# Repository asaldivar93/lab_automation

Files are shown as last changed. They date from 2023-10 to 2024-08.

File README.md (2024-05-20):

## PWM Channels

To control PWM channels you have to create an Output class instance for each channel. The board has up to 6 channels.

```C++
#define N_OUTPUTS 6

Output CH_0(0, PIN_CH0, "pwm", MANUAL, 0);
Output CH_1(1, PIN_CH1, "pwm", MANUAL, 0);
Output CH_2(2, PIN_CH2, "pwm", MANUAL, 0);
Output CH_3(3, PIN_CH3, "pwm", MANUAL, 0);
Output CH_4(4, PIN_CH4, "pwm", MANUAL, 0);
Output CH_5(5, PIN_CH5, "pwm", MANUAL, 0);
Output outputs[N_OUTPUTS] = {CH_0, CH_1, CH_2, CH_3, CH_4, CH_5};
```

Channels can be controled in 4 different modes: {MANUAL, TIMER, PID, ONOFF}. You can initialize this control mode through setter functions.

```C++
Output::set_manual_output(int value);
Output::set_timer(int time_on, int time_off, int value);
Output::set_pid(float *input_value, float setpoint);
Output::set_onoff(float *input_value, int lb, int ub, int value);
```

Example:

```C++
void setup(){
  ...
  outputs[2].set_timer(10, 60, 255);
  ...
}
```

Which is equivalent to doing this:

```C++
void setup(){
  ...
  CH_2.set_timer(10, 60, 255);
  ...
}
```

The PID and ONOFF setters expect a pointer to the measured variable:
```C++
void setup(){
  ...
  outputs[2].set_pid(&inputs[1].value, 50.5);
  outputs[3].set_pid(&inputs[3].value, 1, 1.5, 255);
  ...
}
```
### PID control

The PID controler has important parameters that need to be defined during MCU initialization. This parameters have default values:

- PWM_min_vaule = 0
- PWM_max_value = 255
- Sampling time in microseconds = 250000 (0.250s)
- PID constants:
  - Kp = 100, Ki = 0.2, Kd = 0.

The PID controler uses a simple g-h filter to smooth very noisy signals. The filter uses this formula:

```C++
filtered_input[k] = alpha * current_input + (1 - alpha) * filtered_input[k - 1]
```
where *alpha* [0, 1] controls the strength of the smoothing. *alpha* = 1 **no smoothing at all**, *alpha* close to 0 **very strongth smoothing**. By **default** *alpha* = 0.01.

The default values were tuned to control the temperature of a water reservoir using an external electrical resistance and have been tested to heat water volumes between 50mL and 2L.

These parameters are initialized through setter functions:

```C++
Output::set_sample_time_us(uint32_t sample_time_us);
Output::set_pid_tunings(float Kp, float Ki, float Kd);
Output::set_output_limits(float min, float max);
Output::set_gh_filter(float alpha);
```
example:

```C++
void setup(){
  ...
  outputs[2].set_sample_time_us(250000);
  outputs[2].set_pid_tunings(100, 0.2, 0.);
  outputs[2].set_output_limits(0, 240);
  outputs[2].set_gh_filter(0.01);
  outputs[2].set_pid(&inputs[1].value, 50.5);
  ...
}
```

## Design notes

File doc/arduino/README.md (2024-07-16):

## PWM Channels

To control PWM channels you have to create an Output class instance for each channel. The board has up to 6 channels.

```C++
#define N_PWM 6

Output CH_0(0, PIN_CH0, "pwm", MANUAL, 0);
Output CH_1(1, PIN_CH1, "pwm", MANUAL, 0);
Output CH_2(2, PIN_CH2, "pwm", MANUAL, 0);
Output CH_3(3, PIN_CH3, "pwm", MANUAL, 0);
Output CH_4(4, PIN_CH4, "pwm", MANUAL, 0);
Output CH_5(5, PIN_CH5, "pwm", MANUAL, 0);
Output outputs[N_OUTPUTS] = {CH_0, CH_1, CH_2, CH_3, CH_4, CH_5};
```

Channels can be controled in 4 different modes: {MANUAL, TIMER, PID, ONOFF}. You can initialize this control mode through setter functions.

```C++
Output::set_manual_output(int value);
Output::set_timer(int time_on, int time_off, int value);
Output::set_pid(float *input_value, float setpoint);
Output::set_onoff(float *input_value, int lb, int ub, int value);
```

Example:

```C++
void setup(){
  ...
  outputs[2].set_timer(10, 60, 255);
  ...
}
```

Which is equivalent to doing this:

```C++
void setup(){
  ...
  CH_2.set_timer(10, 60, 255);
  ...
}
```

The PID and ONOFF setters expect a pointer to the measured variable:
```C++
void setup(){
  ...
  outputs[2].set_pid(&inputs[1].value, 50.5);
  outputs[3].set_pid(&inputs[3].value, 1, 1.5, 255);
  ...
}
```
### PID control

The PID controler has important parameters that need to be defined during MCU initialization. This parameters have default values:

- PWM_min_vaule = 0
- PWM_max_value = 255
- Sampling time in microseconds = 250000 (0.250s)
- PID constants:
  - Kp = 100, Ki = 0.2, Kd = 0.

The PID controler uses a simple g-h filter to smooth very noisy signals. The filter uses this formula:

```C++
filtered_input[k] = alpha * current_input + (1 - alpha) * filtered_input[k - 1]
```
where *alpha* [0, 1] controls the strength of the smoothing. *alpha* = 1 **no smoothing at all**, *alpha* close to 0 **very strongth smoothing**. By **default** *alpha* = 0.01.

The default values were tuned to control the temperature of a water reservoir using an external electrical resistance and have been tested to heat water volumes between 50mL and 2L.

These parameters are initialized through setter functions:

```C++
Output::set_sample_time_us(uint32_t sample_time_us);
Output::set_pid_tunings(float Kp, float Ki, float Kd);
Output::set_output_limits(float min, float max);
Output::set_gh_filter(float alpha);
```
example:

```C++
void setup(){
  ...
  outputs[2].set_sample_time_us(250000);
  outputs[2].set_pid_tunings(100, 0.2, 0.);
  outputs[2].set_output_limits(0, 240);
  outputs[2].set_gh_filter(0.01);
  outputs[2].set_pid(&inputs[1].value, 50.5);
  ...
}
```
## I2C Sensors

The board has a TCA9544 I2C multiplexer of 4 channels. This multiplexer allows reading sensors with the same address. You can control the multiplexer with the **Sensors** class

```C++
uint8_t multiplexer_address = 0x70;
float temperature;
Sensors sensors(multiplexer_address);

void setup(){
  Wire.begin();
  Serial.begin(9600);
}

void loop(){
  sensors.set_multiplexer_channel(0);
  temperature = sensors.read_sen0546_temperature();
  Serial.println(temperature);
}
```

Sensors API reference:

```C++
// SEN0546 Temperature and humidity sensor
Sensors::read_sen0546_temperature();
Sensors::read_sen0546_humidity();

// SEN0322 Oxygen Sensor
Sensors::read_sen0322_address_0();
Sensors::read_sen0322_address_1();
Sensors::read_sen0322_address_2();
Sensors::read_sen0322_default();

// MPRLS Pressure sensor
Sensors::read_mprls();
Sensors::set_mprls_range(float p_min, float p_max);

// SEN0343 differential pressure
Sensors::read_sen0343_diffpressure();
```

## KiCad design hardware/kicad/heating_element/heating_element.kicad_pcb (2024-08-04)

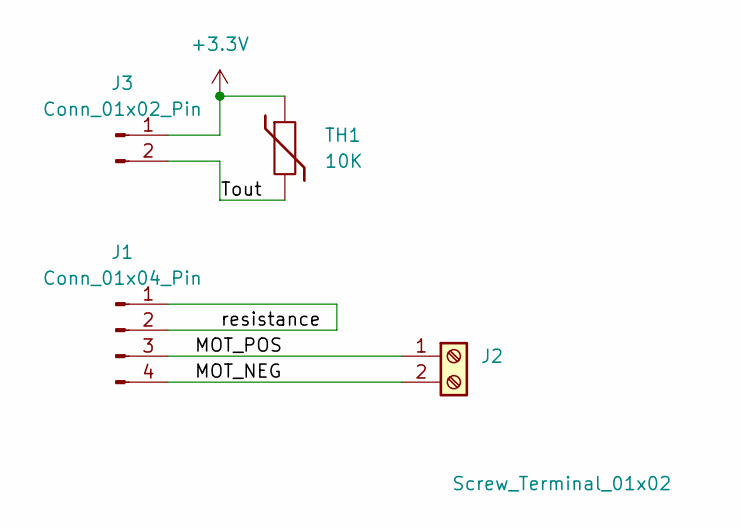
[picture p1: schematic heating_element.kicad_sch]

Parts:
J1: Conn_01x04_Pin; PinHeader_1x04_P2.54mm_Vertical
J2: Screw_Terminal_01x02; TerminalBlock_Phoenix_PT-1,5-2-5.0-H_1x02_P5.00mm_Horizontal
J3: Conn_01x02_Pin; PinHeader_1x02_P2.54mm_Vertical
TH1: 10K; R_Axial_DIN0204_L3.6mm_D1.6mm_P1.90mm_Vertical

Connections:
+3.3V: J3.1, TH1.1
/MOT_NEG: J1.4, J2.2
/MOT_POS: J1.3, J2.1
/Tout: J3.2, TH1.2
/resistance: J1.1, J1.2

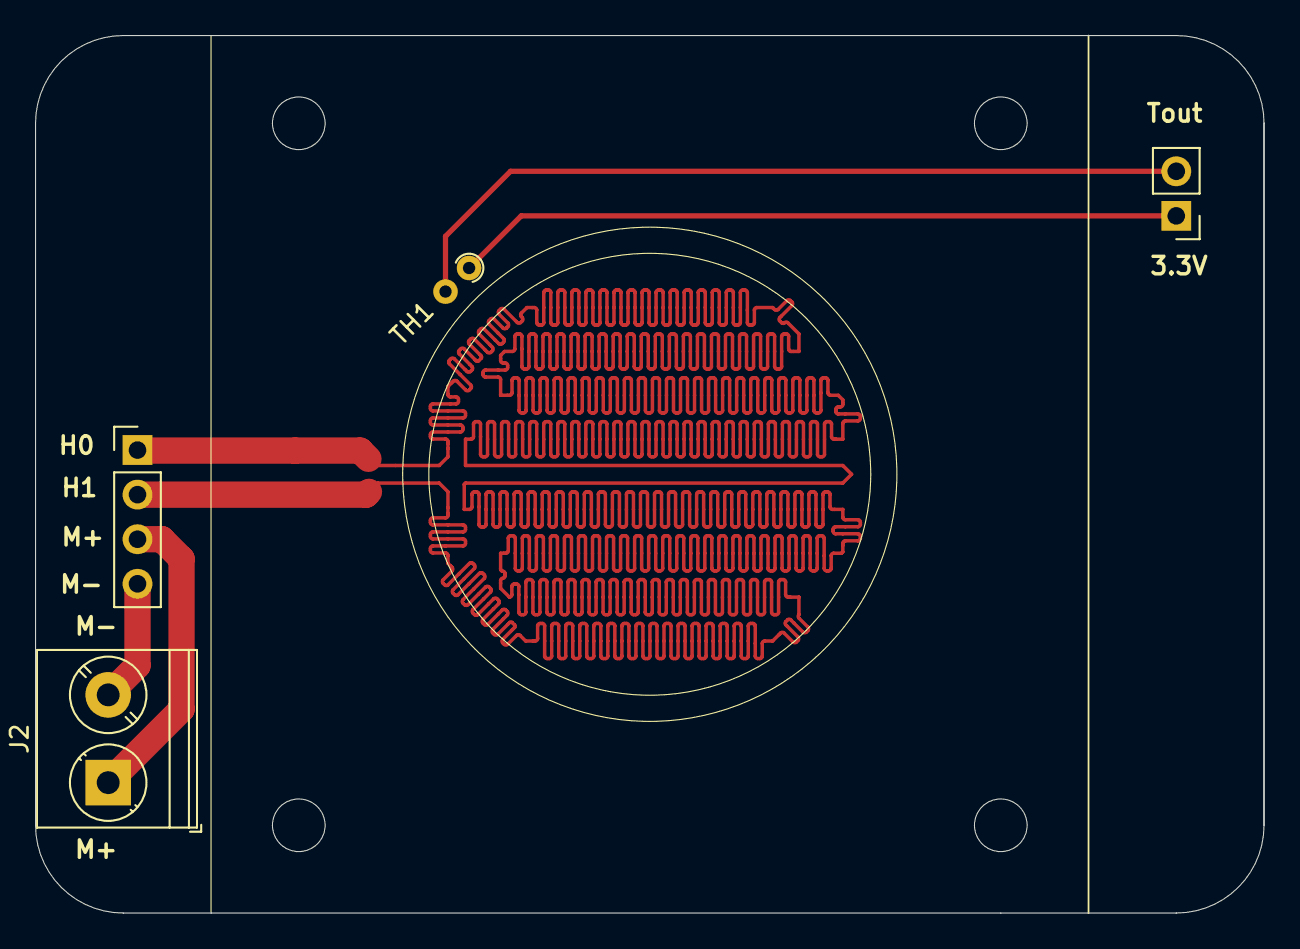
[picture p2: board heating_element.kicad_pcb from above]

Board: 2 copper layers, 70.0 x 50.0 mm, 4 parts (0 on the bottom side), 5 nets.

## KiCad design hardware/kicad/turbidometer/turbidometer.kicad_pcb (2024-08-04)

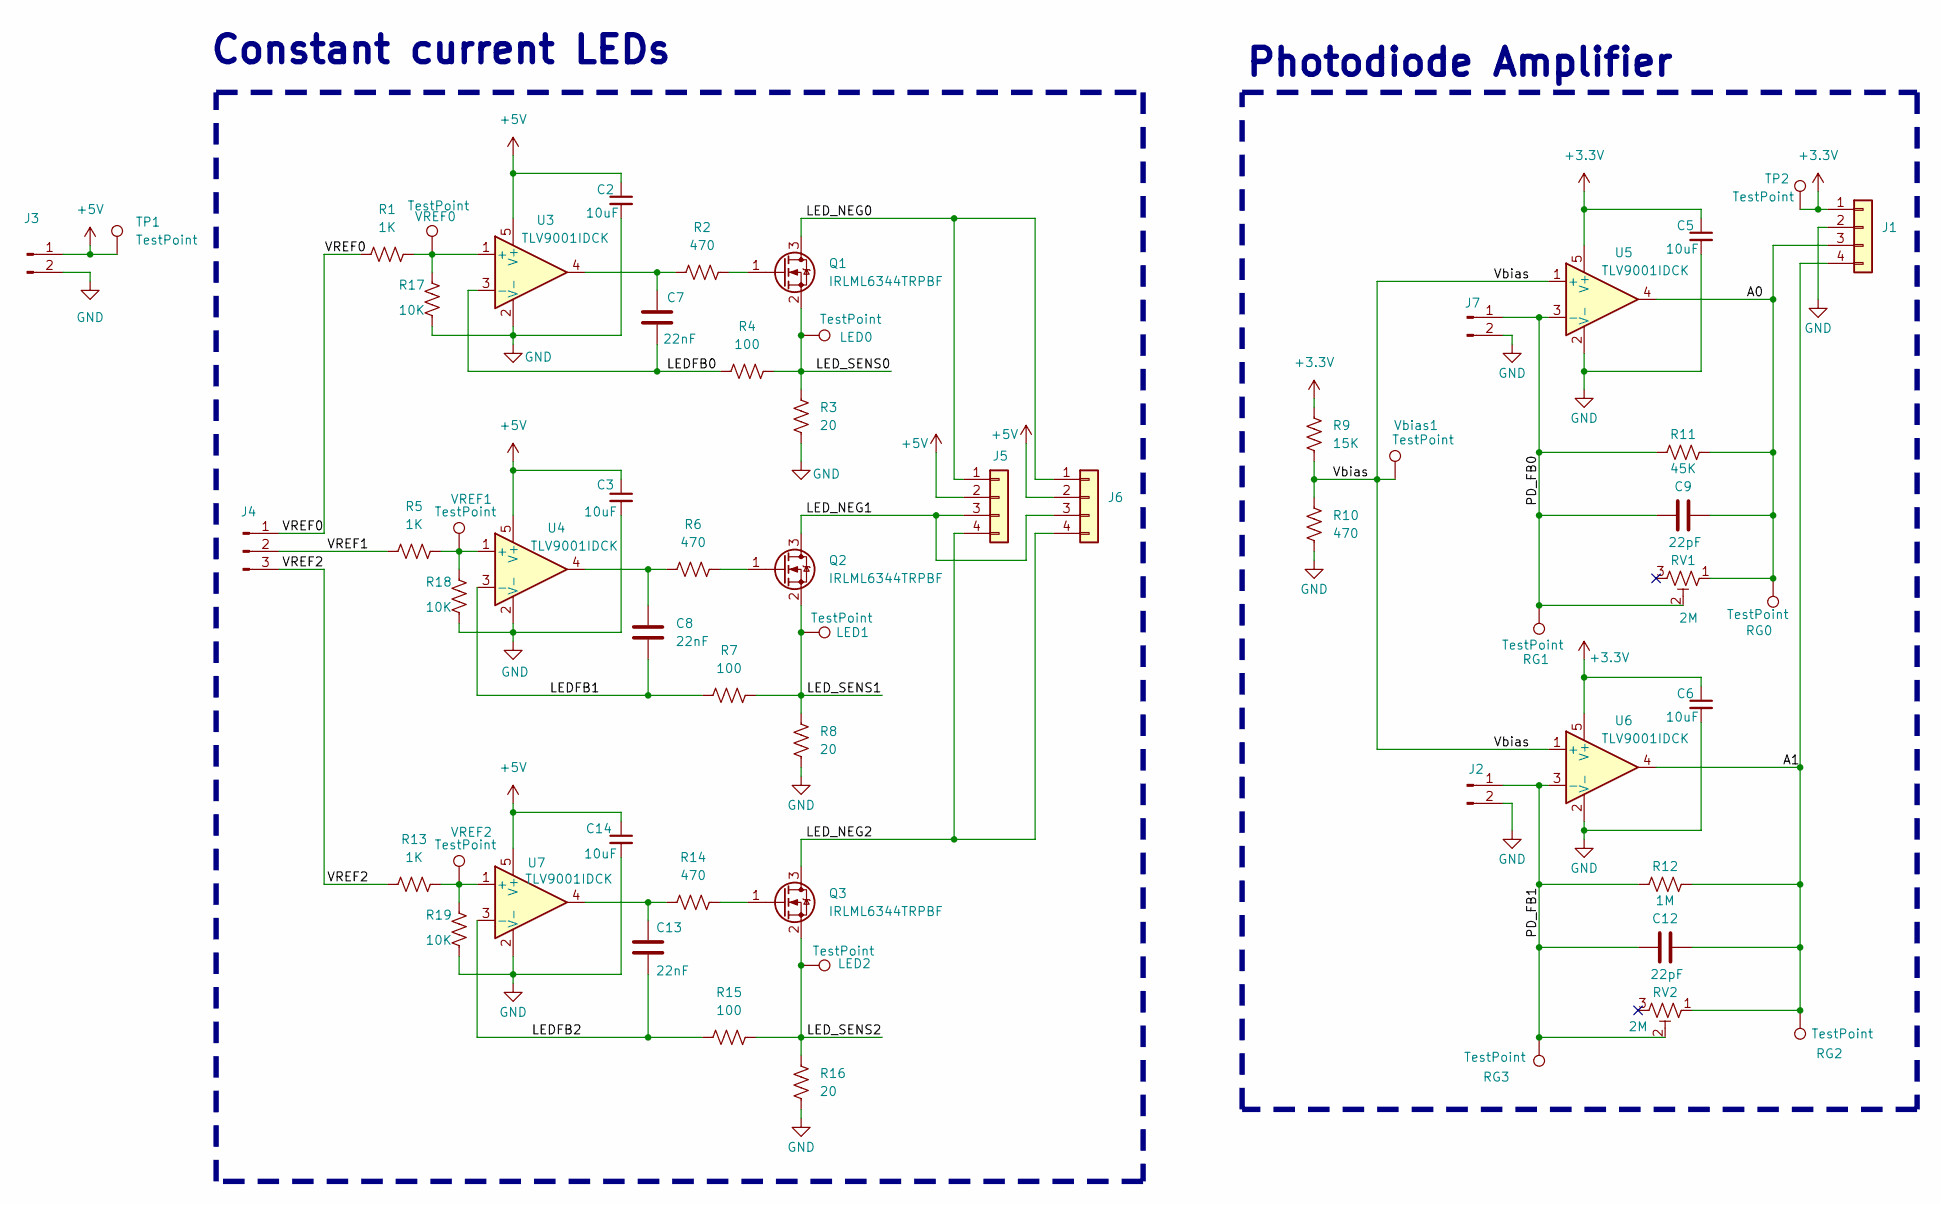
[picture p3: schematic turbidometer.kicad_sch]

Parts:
C2, C3, C5, C6, C14: 10uF; C_0805_2012Metric_Pad1.18x1.45mm_HandSolder
C7, C8, C13: 22nF; C_0805_2012Metric_Pad1.18x1.45mm_HandSolder
C9, C12: 22pF; C_0805_2012Metric_Pad1.18x1.45mm_HandSolder
J1: Conn_01x04; PinHeader_1x04_P2.54mm_Vertical
J2, J7: Conn_01x02_Pin; PinSocket_1x02_P2.54mm_Vertical
J3: Conn_01x02_Pin; PinHeader_1x02_P2.54mm_Vertical
J4: Conn_01x03_Pin; PinHeader_1x03_P2.54mm_Vertical
J5, J6: Conn_01x04; PinSocket_1x04_P2.54mm_Vertical
LED0, LED1, LED2: TestPoint; TestPoint_THTPad_1.5x1.5mm_Drill0.7mm
Q1, Q2, Q3: IRLML6344TRPBF; SOT-23_Handsoldering
R1, R5, R13: 1K; R_0805_2012Metric_Pad1.20x1.40mm_HandSolder
R2, R6, R10, R14: 470; R_0805_2012Metric_Pad1.20x1.40mm_HandSolder
R3, R8, R16: 20; R_0805_2012Metric_Pad1.20x1.40mm_HandSolder
R4, R7, R15: 100; R_0805_2012Metric_Pad1.20x1.40mm_HandSolder
R9: 15K; R_0805_2012Metric_Pad1.20x1.40mm_HandSolder
R11: 45K; R_0805_2012Metric_Pad1.20x1.40mm_HandSolder
R12: 1M; R_0805_2012Metric_Pad1.20x1.40mm_HandSolder
R17, R18, R19: 10K; R_0805_2012Metric_Pad1.20x1.40mm_HandSolder
RG0, RG1, RG2, RG3: TestPoint; TestPoint_THTPad_1.5x1.5mm_Drill0.7mm
RV1, RV2: 2M; Potentiometer_Bourns_3214W_Vertical
TP1, TP2: TestPoint; TestPoint_Pad_1.0x1.0mm
U3, U4, U5, U6, U7: TLV9001IDCK; SOT-353_SC-70-5
VREF0, VREF1, VREF2: TestPoint; TestPoint_THTPad_1.5x1.5mm_Drill0.7mm
Vbias1: TestPoint; TestPoint_Pad_1.0x1.0mm

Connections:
+3.3V: C5.1, C6.1, J1.1, R9.1, TP2.1, U5.5 (V+), U6.5 (V+)
+5V: C2.1, C3.1, C14.1, J3.1, J5.2, J6.2, TP1.1, U3.5 (V+), U4.5 (V+), U7.5 (V+)
/A0: C9.2, J1.3, R11.1, RG0.1, RV1.1, U5.4
/A1: C12.2, J1.4, R12.1, RG2.1, RV2.1, U6.4
/LEDFB0: C7.2, R4.2, U3.3 (-)
/LEDFB1: C8.2, R7.2, U4.3 (-)
/LEDFB2: C13.2, R15.2, U7.3 (-)
/LED_NEG0: J5.1, J6.1, Q1.3 (D)
/LED_NEG1: J5.3, J6.3, Q2.3 (D)
/LED_NEG2: J5.4, J6.4, Q3.3 (D)
/LED_SENS0: LED0.1, Q1.2 (S), R3.1, R4.1
/LED_SENS1: LED1.1, Q2.2 (S), R7.1, R8.1
/LED_SENS2: LED2.1, Q3.2 (S), R15.1, R16.1
/PD_FB0: C9.1, J7.1, R11.2, RG1.1, RV1.2, U5.3 (-)
/PD_FB1: C12.1, J2.1, R12.2, RG3.1, RV2.2, U6.3 (-)
/VREF0: J4.1, R1.2
/VREF1: J4.2, R5.2
/VREF2: J4.3, R13.2
/Vbias: R9.2, R10.1, U5.1 (+), U6.1 (+), Vbias1.1
GND: C2.2, C3.2, C5.2, C6.2, C14.2, J1.2, J2.2, J3.2, J7.2, R3.2, R8.2, R10.2, R16.2, R17.2, R18.2, R19.2, U3.2 (V-), U4.2 (V-), U5.2 (V-), U6.2 (V-), U7.2 (V-)
unnamed: C7.1, R2.2, U3.4
unnamed: C8.1, R6.2, U4.4
unnamed: C13.1, R14.2, U7.4
unnamed: Q1.1 (G), R2.1
unnamed: Q2.1 (G), R6.1
unnamed: Q3.1 (G), R14.1
unnamed: R1.1, R17.1, U3.1 (+), VREF0.1
unnamed: R5.1, R18.1, U4.1 (+), VREF1.1
unnamed: R13.1, R19.1, U7.1 (+), VREF2.1

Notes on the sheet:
Constant current LEDs
Photodiode Amplifier

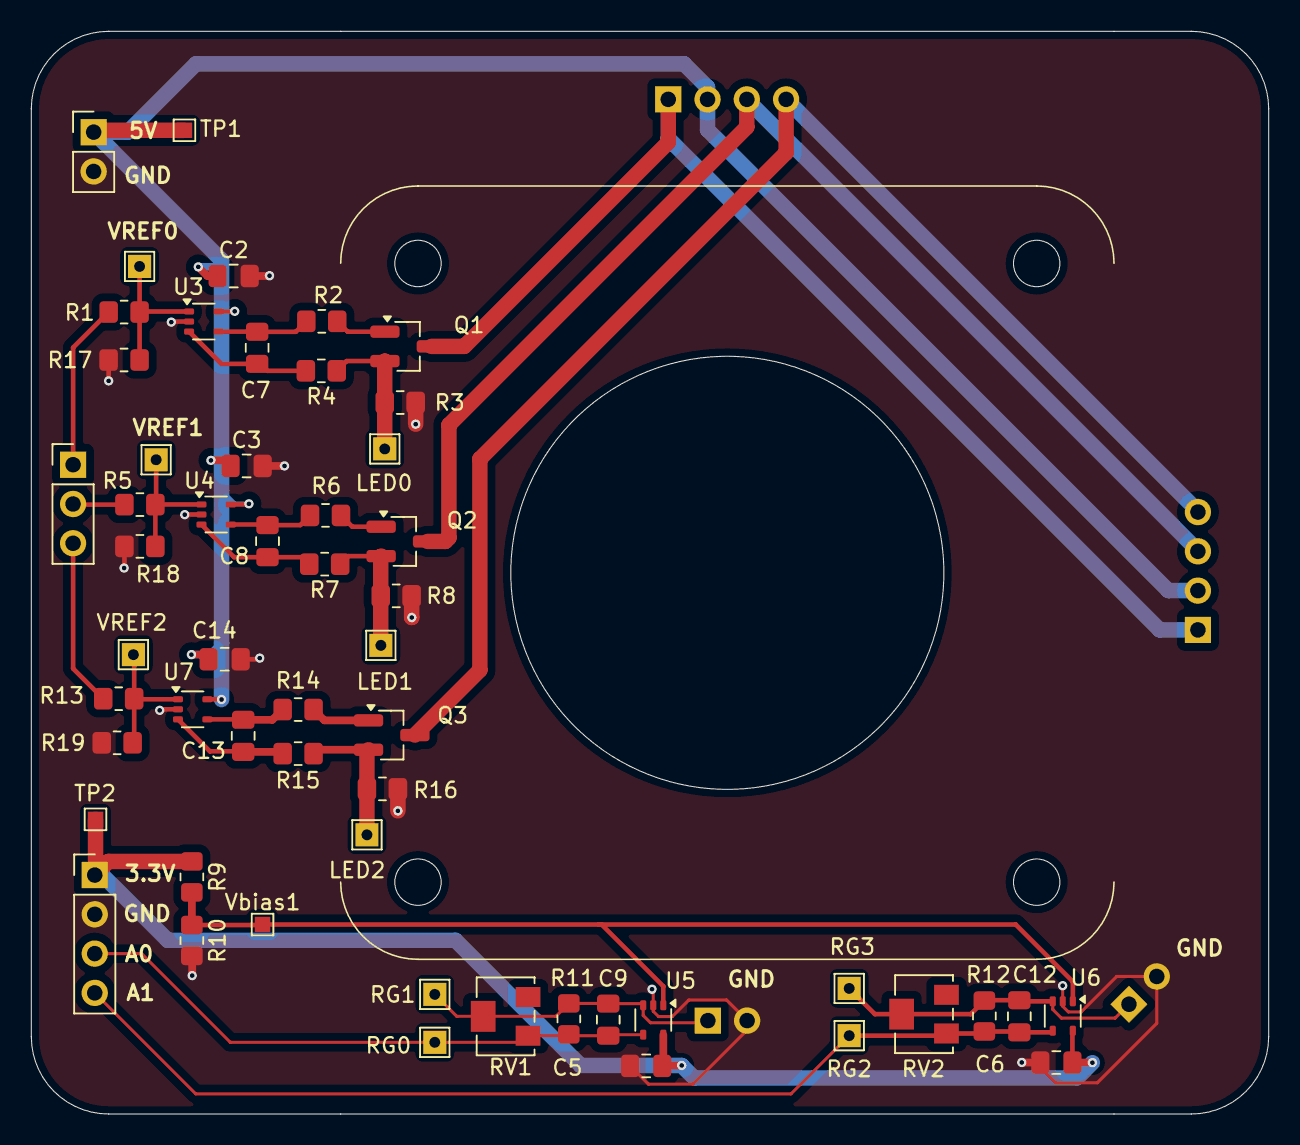
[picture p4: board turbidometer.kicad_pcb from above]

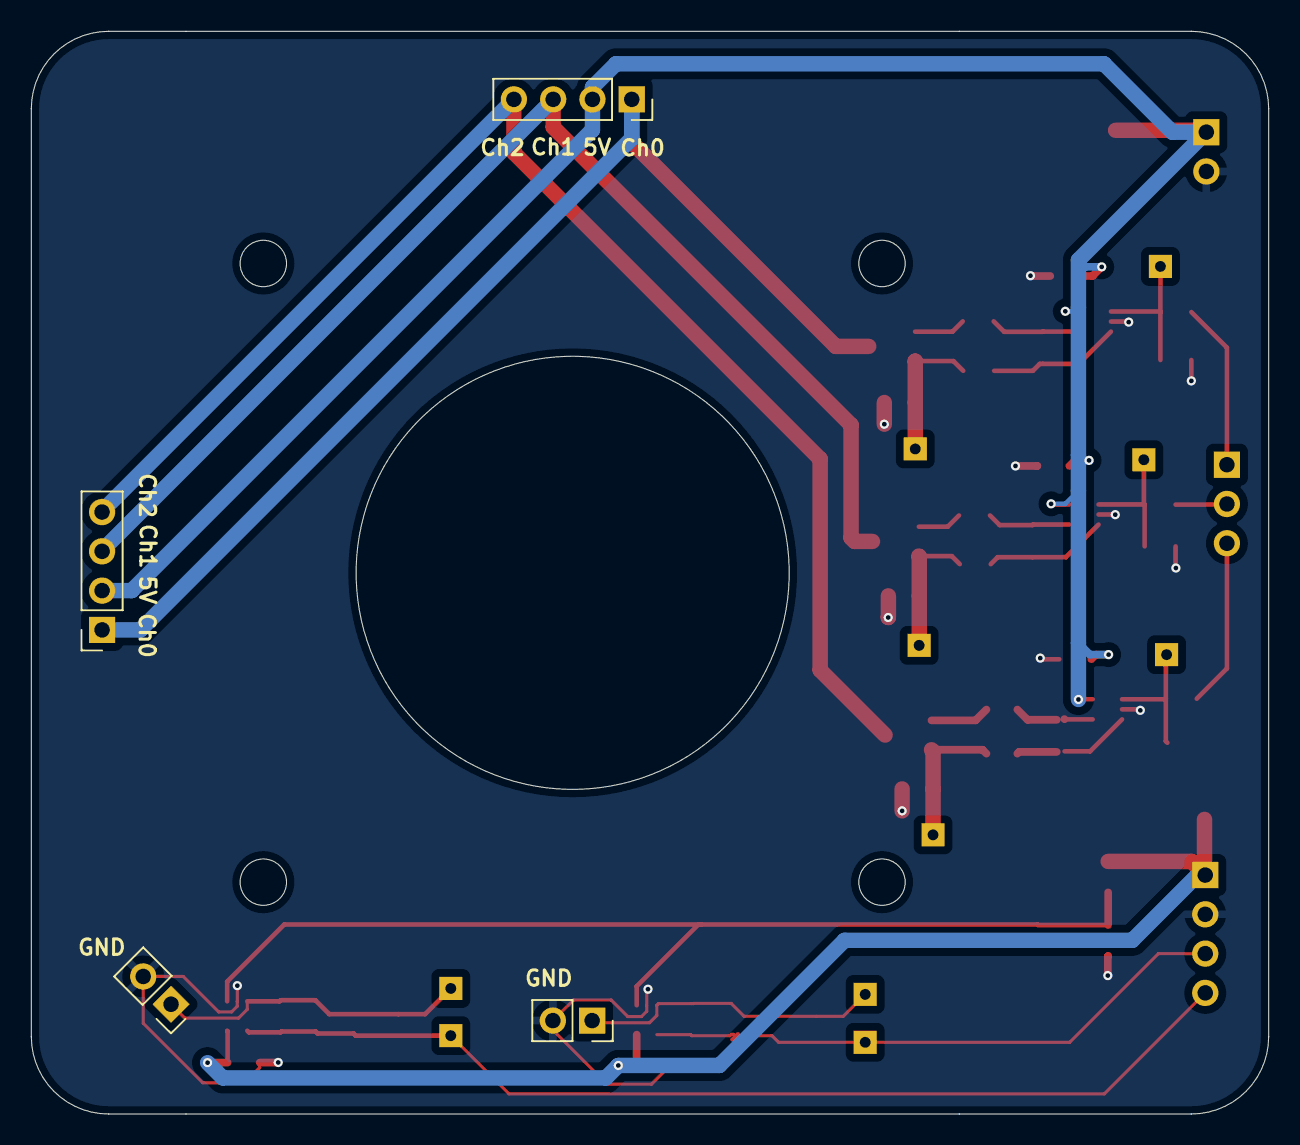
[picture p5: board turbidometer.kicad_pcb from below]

Board: 2 copper layers, 80.0 x 70.0 mm, 59 parts (4 on the bottom side), 29 nets.

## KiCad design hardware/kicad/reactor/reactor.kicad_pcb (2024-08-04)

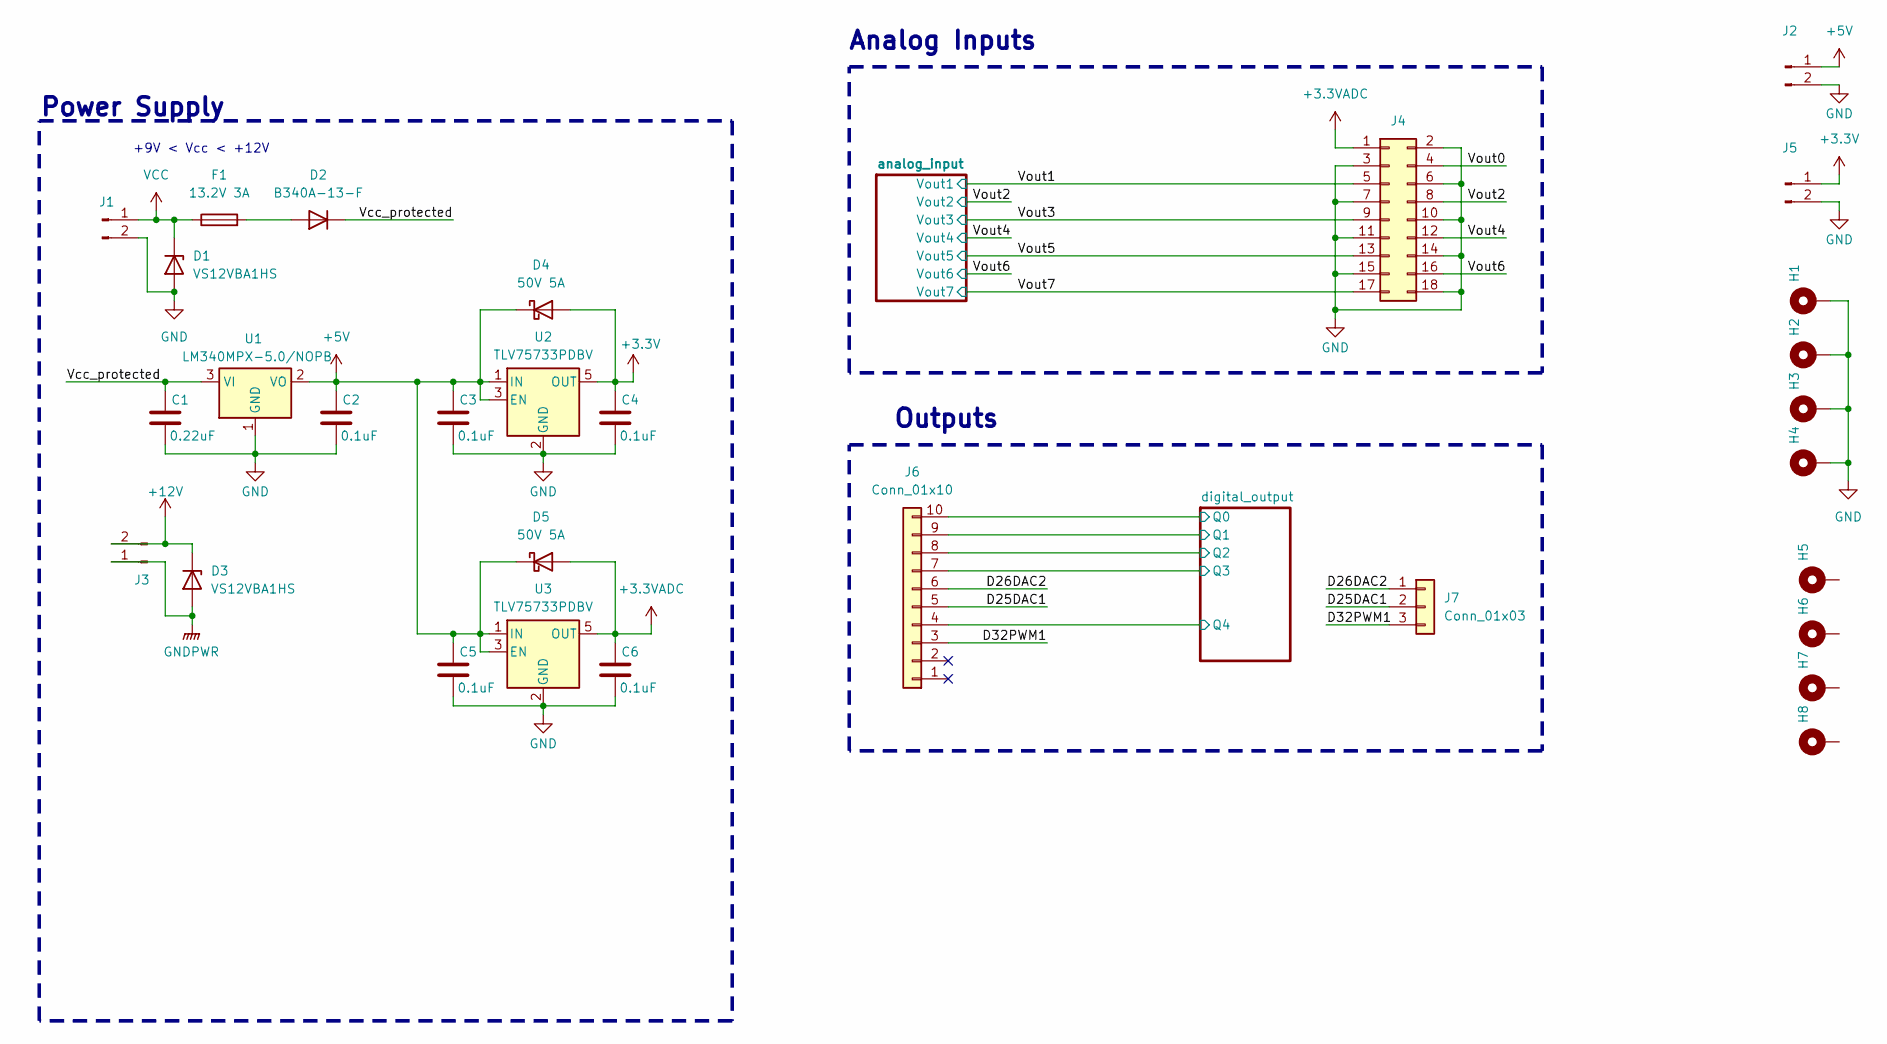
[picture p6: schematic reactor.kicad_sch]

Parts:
C1: 0.22uF; C_0805_2012Metric_Pad1.18x1.45mm_HandSolder
C2, C3, C4, C5, C6: 0.1uF; C_1206_3216Metric
D1, D3: VS12VBA1HS; D_0603_1608Metric_Pad1.05x0.95mm_HandSolder
D2: B340A-13-F; D_SMA
D4, D5: 50V 5A; D_SMA
F1: 13.2V 3A; Fuse_1206_3216Metric
H1, H2, H3, H4, H5, H6, H7, H8: MountingHole_Pad; MountingHole_3.2mm_M3_DIN965_Pad_TopBottom
J1, J2: Conn_01x02_Pin; PhoenixContact_MC_1,5_2-G-3.81_1x02_P3.81mm_Horizontal
J3: Conn_01x02_Pin; AMASS_XT60-F_1x02_P7.20mm_Vertical
J4: Conn_02x09_Odd_Even; PinSocket_2x09_P2.54mm_Vertical
J5: Conn_01x02_Pin; PinSocket_1x02_P2.54mm_Vertical
J6: Conn_01x10; PinSocket_1x10_P2.54mm_Vertical
J7: Conn_01x03; PhoenixContact_MC_1,5_3-G-3.81_1x03_P3.81mm_Horizontal
U1: LM340MPX-5.0/NOPB; SOT-223-3_TabPin2
U2, U3: TLV75733PDBV; SOT-23-5

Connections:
+3.3V: C4.1, D4.2 (A), J5.1, U2.5 (OUT)
+3.3VADC: C6.1, D5.2 (A), J4.1, U3.5 (OUT); also elsewhere on the board
+5V: C2.1, C3.1, C5.1, D4.1 (K), D5.1 (K), J2.1, U1.2 (VO), U2.1 (IN), U2.3 (EN), U3.1 (IN), U3.3 (EN)
+12V: D3.1 (K), J3.2; also elsewhere on the board
/D25DAC1: J6.5, J7.2
/D26DAC2: J6.6, J7.1
/D32PWM1: J6.3, J7.3
/Vcc_protected: C1.1, D2.1 (K), U1.3 (VI)
/Vout0: J4.4
/Vout1: J4.5; also elsewhere on the board
/Vout2: J4.8; also elsewhere on the board
/Vout3: J4.9; also elsewhere on the board
/Vout4: J4.12; also elsewhere on the board
/Vout5: J4.13; also elsewhere on the board
/Vout6: J4.16; also elsewhere on the board
/Vout7: J4.17; also elsewhere on the board
/digital_output/Q0: J6.10; also elsewhere on the board
/digital_output/Q1: J6.9; also elsewhere on the board
/digital_output/Q2: J6.8; also elsewhere on the board
/digital_output/Q3: J6.7; also elsewhere on the board
/digital_output/Q4: J6.4; also elsewhere on the board
GND: C1.2, C2.2, C3.2, C4.2, C5.2, C6.2, D1.2 (A), H1.1, H2.1, H3.1, H4.1, J1.2, J2.2, J4.2, J4.3, J4.6, J4.7, J4.10, J4.11, J4.14, J4.15, J4.18, J5.2, U1.1 (GND), U2.2 (GND), U3.2 (GND); also elsewhere on the board
GNDPWR: D3.2 (A), J3.1; also elsewhere on the board
unnamed: D2.2 (A), F1.2
VCC: D1.1 (K), F1.1, J1.1

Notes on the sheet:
Outputs
+9V < Vcc < +12V
Analog Inputs
Power Supply

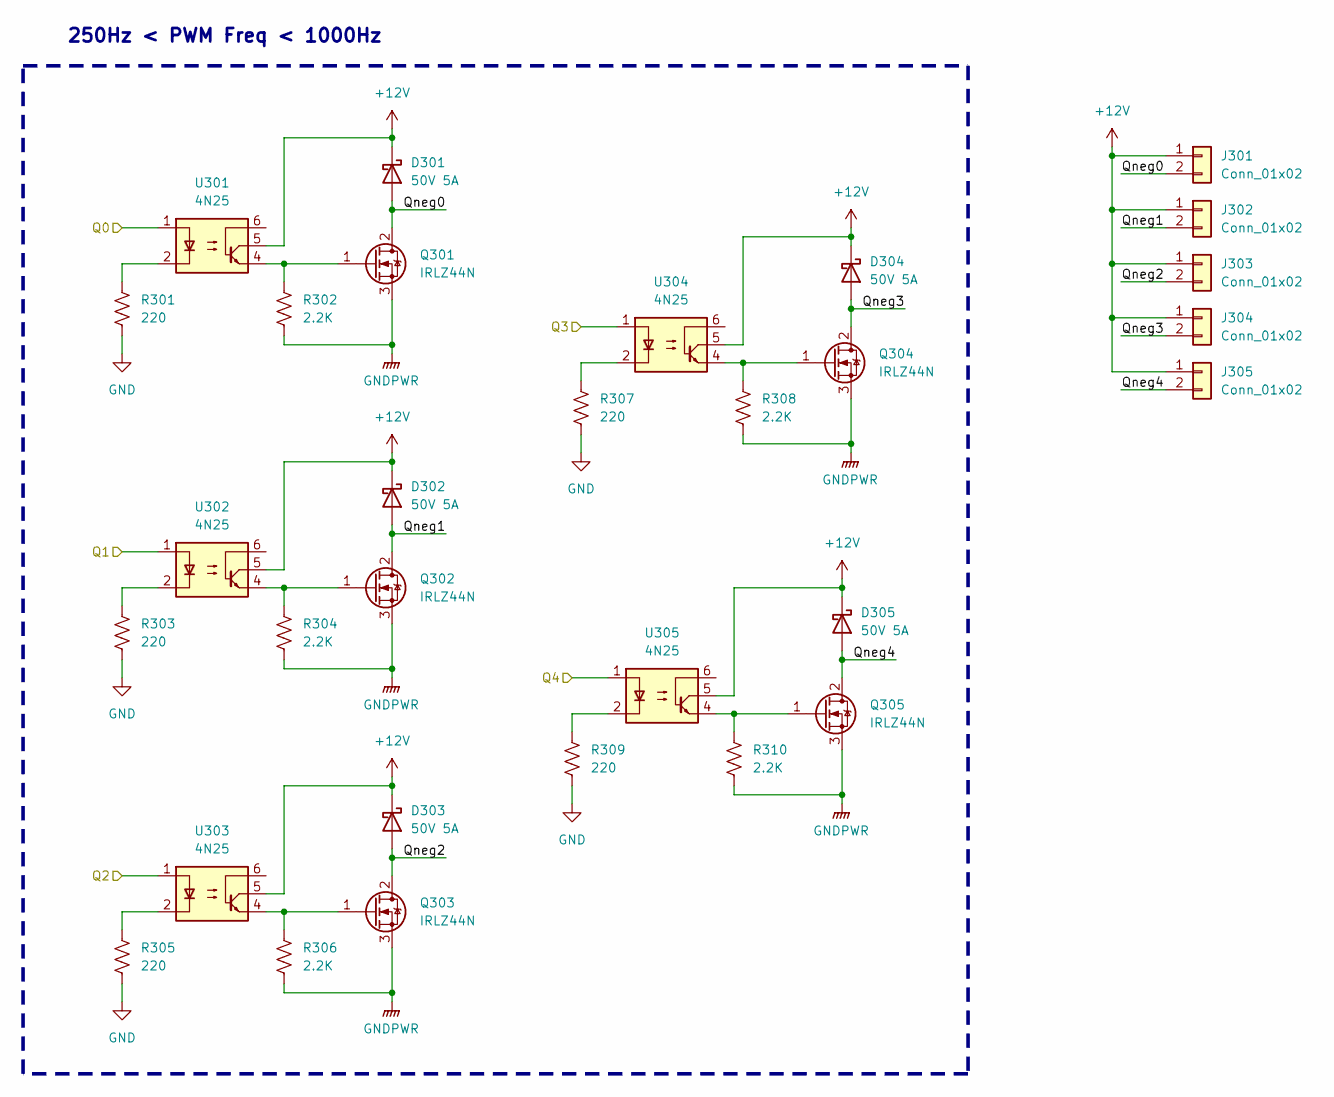
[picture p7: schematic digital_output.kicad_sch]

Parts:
D301, D302, D303, D304, D305: 50V 5A; D_SMA_Handsoldering
J301, J302, J303, J304, J305: Conn_01x02; PhoenixContact_MC_1,5_2-G-3.81_1x02_P3.81mm_Horizontal
Q301, Q302, Q303, Q304, Q305: IRLZ44N; TO-220-3_Vertical
R301, R303, R305, R307, R309: 220; R_Axial_DIN0204_L3.6mm_D1.6mm_P5.08mm_Horizontal
R302, R304, R306, R308, R310: 2.2K; R_Axial_DIN0204_L3.6mm_D1.6mm_P5.08mm_Horizontal
U301, U302, U303, U304, U305: 4N25; DIP-6_W7.62mm_Socket

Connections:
+12V: D301.1 (K), D302.1 (K), D303.1 (K), D304.1 (K), D305.1 (K), J301.1, J302.1, J303.1, J304.1, J305.1, U301.5, U302.5, U303.5, U304.5, U305.5; also elsewhere on the board
/digital_output/Q0: U301.1; also elsewhere on the board
/digital_output/Q1: U302.1; also elsewhere on the board
/digital_output/Q2: U303.1; also elsewhere on the board
/digital_output/Q3: U304.1; also elsewhere on the board
/digital_output/Q4: U305.1; also elsewhere on the board
/digital_output/Qneg0: D301.2 (A), J301.2, Q301.2 (D)
/digital_output/Qneg1: D302.2 (A), J302.2, Q302.2 (D)
/digital_output/Qneg2: D303.2 (A), J303.2, Q303.2 (D)
/digital_output/Qneg3: D304.2 (A), J304.2, Q304.2 (D)
/digital_output/Qneg4: D305.2 (A), J305.2, Q305.2 (D)
GND: R301.2, R303.2, R305.2, R307.2, R309.2; also elsewhere on the board
GNDPWR: Q301.3 (S), Q302.3 (S), Q303.3 (S), Q304.3 (S), Q305.3 (S), R302.2, R304.2, R306.2, R308.2, R310.2; also elsewhere on the board
unnamed: Q301.1 (G), R302.1, U301.4
unnamed: Q302.1 (G), R304.1, U302.4
unnamed: Q303.1 (G), R306.1, U303.4
unnamed: Q304.1 (G), R308.1, U304.4
unnamed: Q305.1 (G), R310.1, U305.4
unnamed: R301.1, U301.2
unnamed: R303.1, U302.2
unnamed: R305.1, U303.2
unnamed: R307.1, U304.2
unnamed: R309.1, U305.2

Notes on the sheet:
250Hz < PWM Freq < 1000Hz

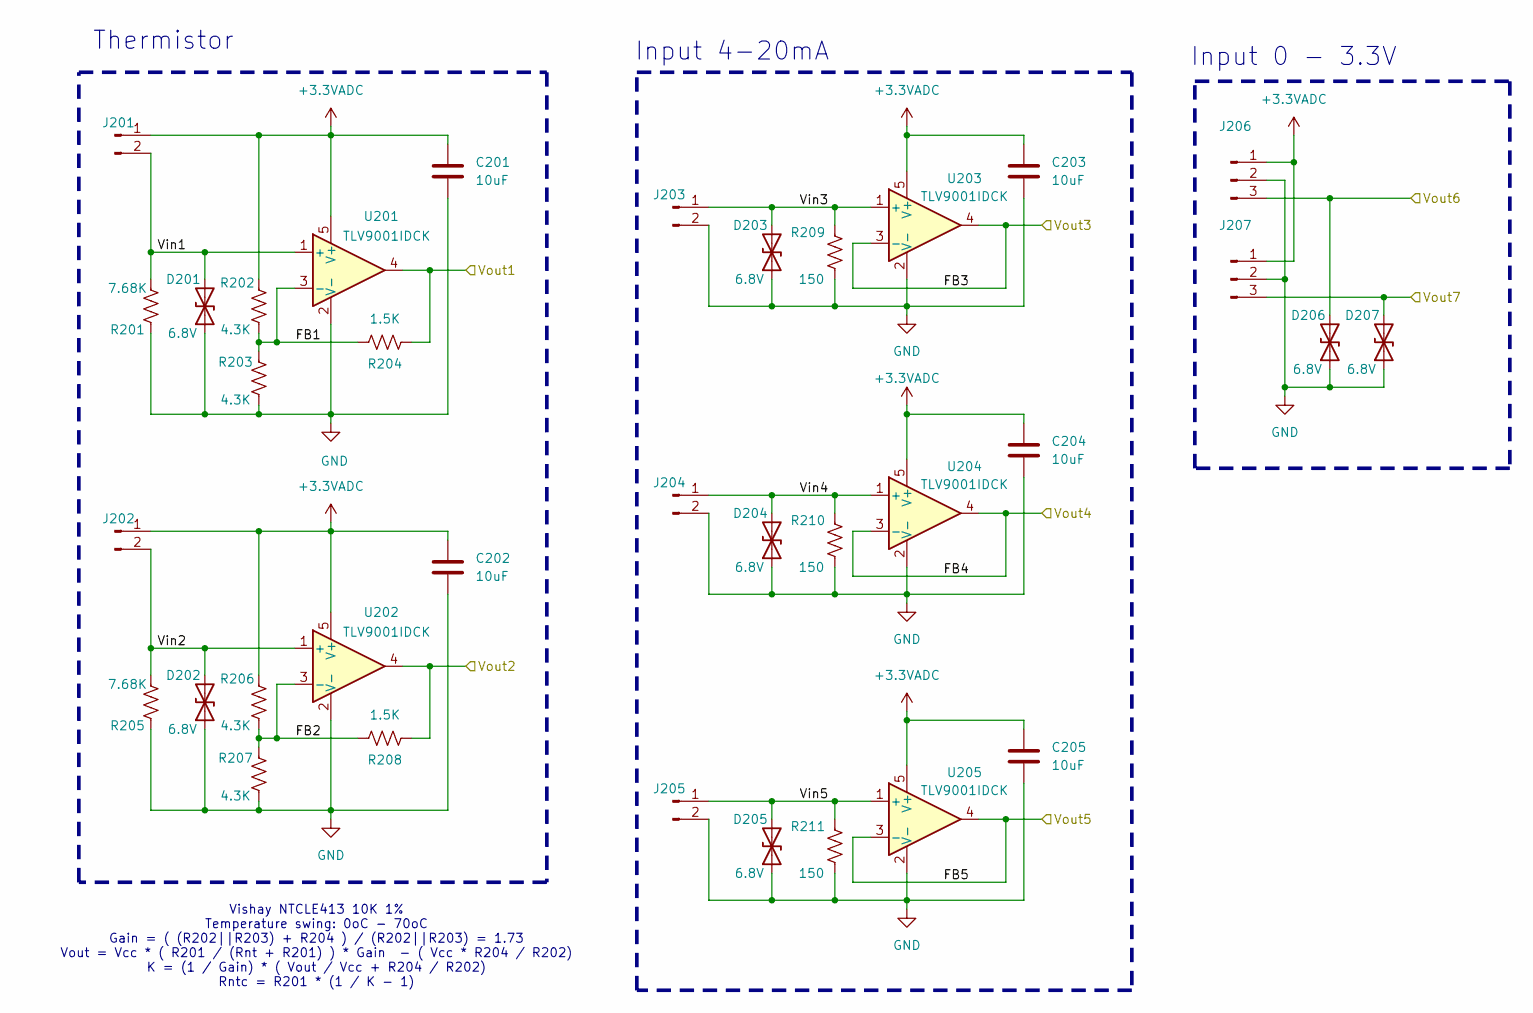
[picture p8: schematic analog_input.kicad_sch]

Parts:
C201, C202, C203, C204, C205: 10uF; C_0805_2012Metric_Pad1.18x1.45mm_HandSolder
D201, D202, D203, D204, D205, D206, D207: 6.8V; D_SOD-523
J201, J202, J203, J204, J205: Conn_01x02_Pin; PhoenixContact_MC_1,5_2-G-3.81_1x02_P3.81mm_Horizontal
J206, J207: Conn_01x03_Pin; PhoenixContact_MC_1,5_3-G-3.81_1x03_P3.81mm_Horizontal
R201, R205: 7.68K; R_0805_2012Metric_Pad1.20x1.40mm_HandSolder
R202, R203, R206, R207: 4.3K; R_0805_2012Metric_Pad1.20x1.40mm_HandSolder
R204, R208: 1.5K; R_0805_2012Metric_Pad1.20x1.40mm_HandSolder
R209, R210, R211: 150; R_0805_2012Metric_Pad1.20x1.40mm_HandSolder
U201, U202, U203, U204, U205: TLV9001IDCK; SOT-353_SC-70-5

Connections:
+3.3VADC: C201.1, C202.1, C203.1, C204.1, C205.1, J201.1, J202.1, J206.1, J207.1, R202.2, R206.2, U201.5 (V+), U202.5 (V+), U203.5 (V+), U204.5 (V+), U205.5 (V+); also elsewhere on the board
/Vout1: R204.2, U201.4; also elsewhere on the board
/Vout2: R208.2, U202.4; also elsewhere on the board
/Vout3: U203.3 (-), U203.4; also elsewhere on the board
/Vout4: U204.3 (-), U204.4; also elsewhere on the board
/Vout5: U205.3 (-), U205.4; also elsewhere on the board
/Vout6: D206.2 (A2), J206.3; also elsewhere on the board
/Vout7: D207.2 (A2), J207.3; also elsewhere on the board
/analog_input/FB1: R202.1, R203.2, R204.1, U201.3 (-)
/analog_input/FB2: R206.1, R207.2, R208.1, U202.3 (-)
/analog_input/Vin1: D201.2 (A2), J201.2, R201.2, U201.1 (+)
/analog_input/Vin2: D202.2 (A2), J202.2, R205.2, U202.1 (+)
/analog_input/Vin3: D203.2 (A2), J203.1, R209.2, U203.1 (+)
/analog_input/Vin4: D204.2 (A2), J204.1, R210.2, U204.1 (+)
/analog_input/Vin5: D205.2 (A2), J205.1, R211.2, U205.1 (+)
GND: C201.2, C202.2, C203.2, C204.2, C205.2, D201.1 (A1), D202.1 (A1), D203.1 (A1), D204.1 (A1), D205.1 (A1), D206.1 (A1), D207.1 (A1), J203.2, J204.2, J205.2, J206.2, J207.2, R201.1, R203.1, R205.1, R207.1, R209.1, R210.1, R211.1, U201.2 (V-), U202.2 (V-), U203.2 (V-), U204.2 (V-), U205.2 (V-); also elsewhere on the board

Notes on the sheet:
Vishay NTCLE413 10K 1% Temperature swing: 0oC - 70oC Gain = ( (R202||R203) + R204 ) / (R202||R203) = 1.73 Vout = Vcc * ( R201 / (Rnt + R201) ) * Gain - ( Vcc * R204 / R202) K = (1 / Gain) * ( Vout / Vcc + R204 / R202) Rntc = R201 * (1 / K - 1)
Input 4-20mA
Input 0 - 3.3V
Thermistor

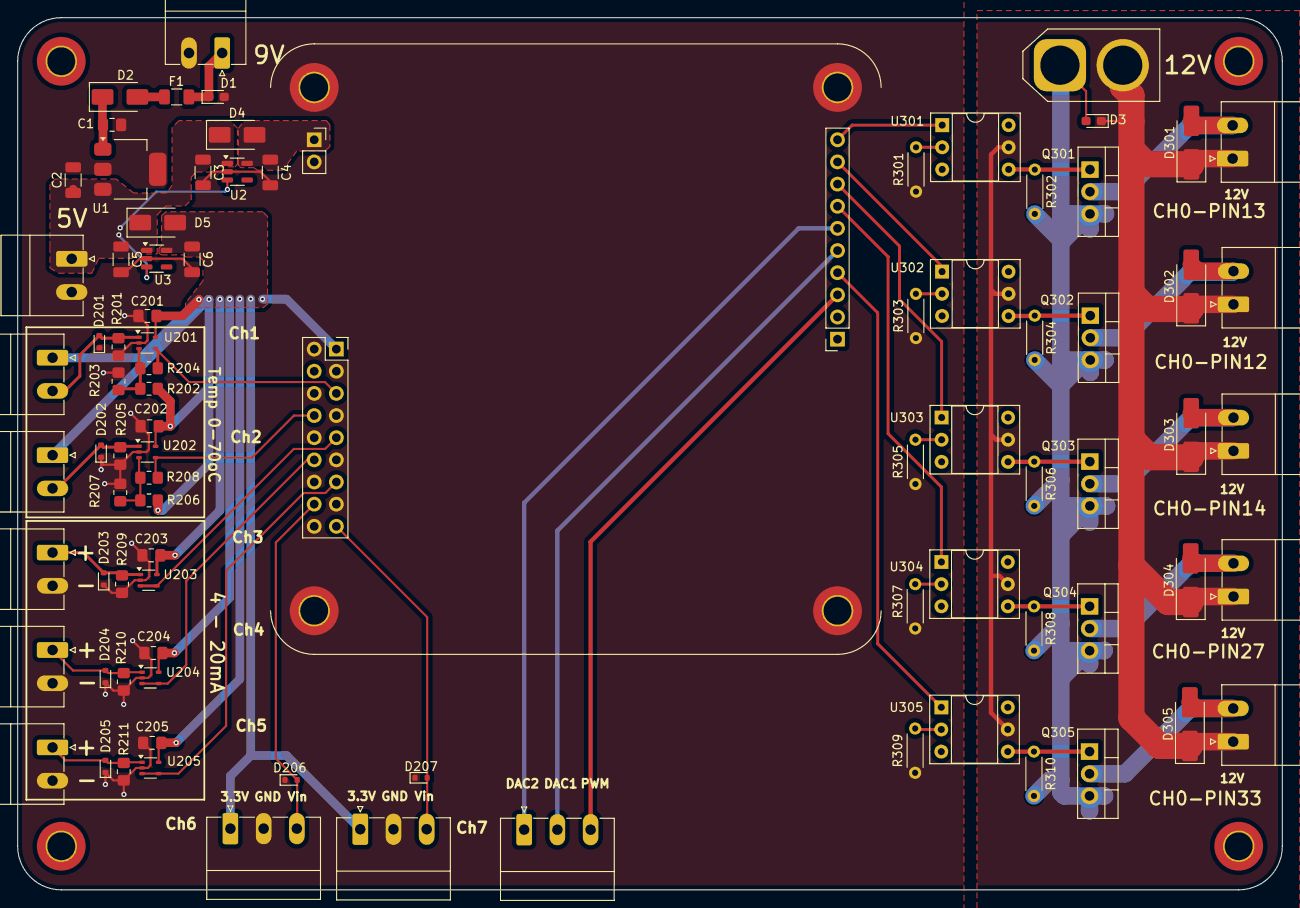
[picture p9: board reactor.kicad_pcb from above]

Board: 2 copper layers, 145.0 x 100.0 mm, 95 parts (0 on the bottom side), 46 nets.

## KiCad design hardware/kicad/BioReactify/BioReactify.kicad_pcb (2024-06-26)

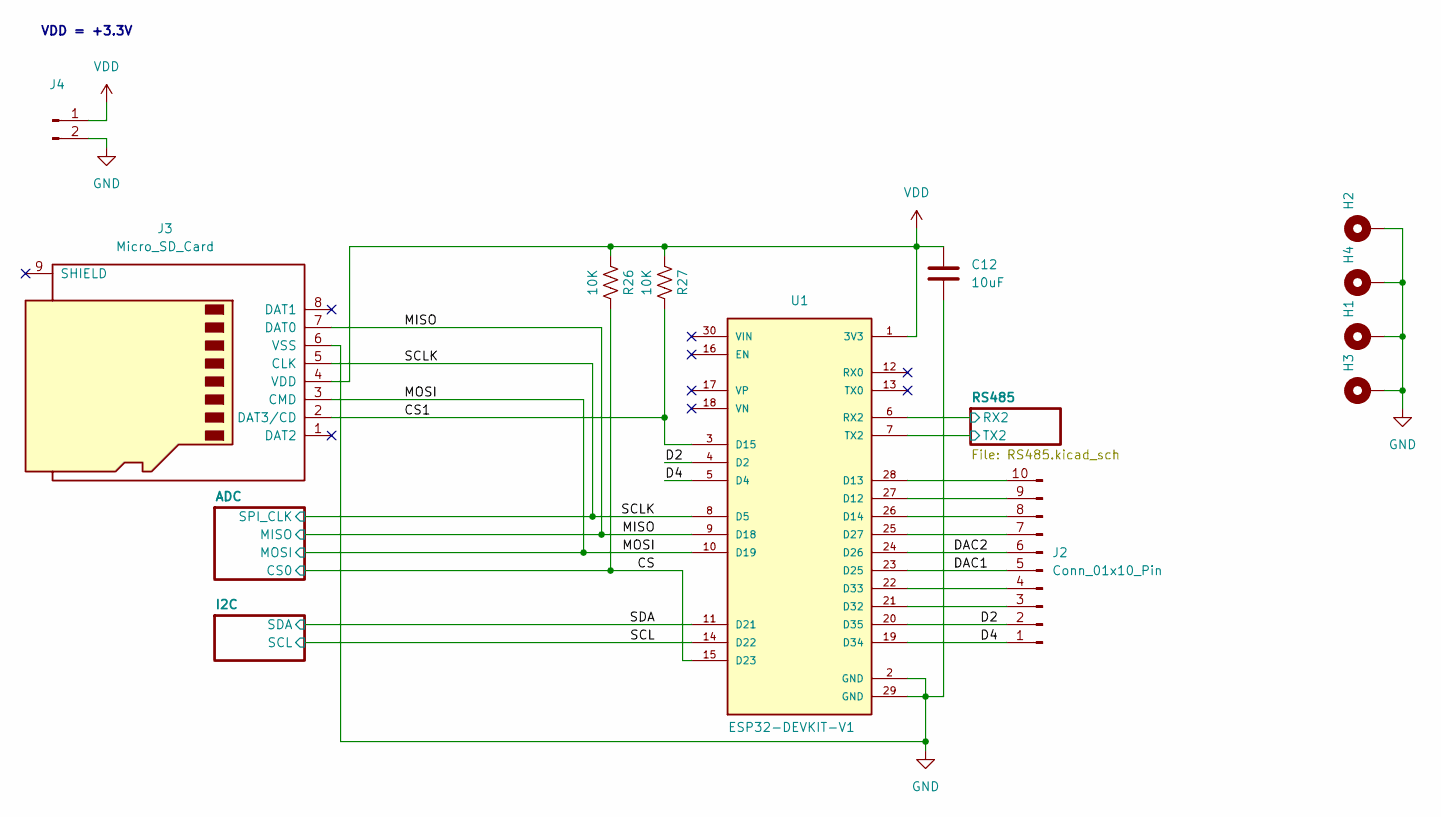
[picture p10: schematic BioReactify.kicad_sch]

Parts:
C12: 10uF; C_0805_2012Metric
H1, H2, H3, H4: MountingHole_Pad; MountingHole_3.2mm_M3_DIN965_Pad_TopBottom
J2: Conn_01x10_Pin; PinHeader_1x10_P2.54mm_Vertical
J3: Micro_SD_Card; TF-SMD_THD2528-11SD-GF
J4: Conn_01x02_Pin; PinHeader_1x02_P2.54mm_Vertical
R26, R27: 10K; R_0805_2012Metric_Pad1.20x1.40mm_HandSolder
U1: ESP32-DEVKIT-V1; MODULE_ESP32_DEVKIT_V1; PARTREV N/A

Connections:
/CS: R26.2, U1.15 (D23); also elsewhere on the board
/CS1: J3.2 (DAT3/CD), R27.2, U1.3 (D15)
/D2: J2.2, U1.4 (D2), U1.20 (D35)
/D4: J2.1, U1.5 (D4), U1.19 (D34)
/DAC1: J2.5, U1.23 (D25)
/DAC2: J2.6, U1.24 (D26)
/MISO: J3.7 (DAT0), U1.9 (D18); also elsewhere on the board
/MOSI: J3.3 (CMD), U1.10 (D19); also elsewhere on the board
/RS485/RX2: U1.6 (RX2); also elsewhere on the board
/RS485/TX2: U1.7 (TX2); also elsewhere on the board
/SCL: U1.14 (D22); also elsewhere on the board
/SCLK: J3.5 (CLK), U1.8 (D5); also elsewhere on the board
/SDA: U1.11 (D21); also elsewhere on the board
GND: C12.2, H1.1, H2.1, H3.1, H4.1, J3.6 (VSS), J4.2, U1.2 (GND), U1.29 (GND); also elsewhere on the board
unnamed: J2.3, U1.21 (D32)
unnamed: J2.4, U1.22 (D33)
unnamed: J2.7, U1.25 (D27)
unnamed: J2.8, U1.26 (D14)
unnamed: J2.9, U1.27 (D12)
unnamed: J2.10, U1.28 (D13)
VDD: C12.1, J3.4 (VDD), J4.1, R26.1, R27.1, U1.1 (3V3); also elsewhere on the board

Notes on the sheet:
VDD = +3.3V

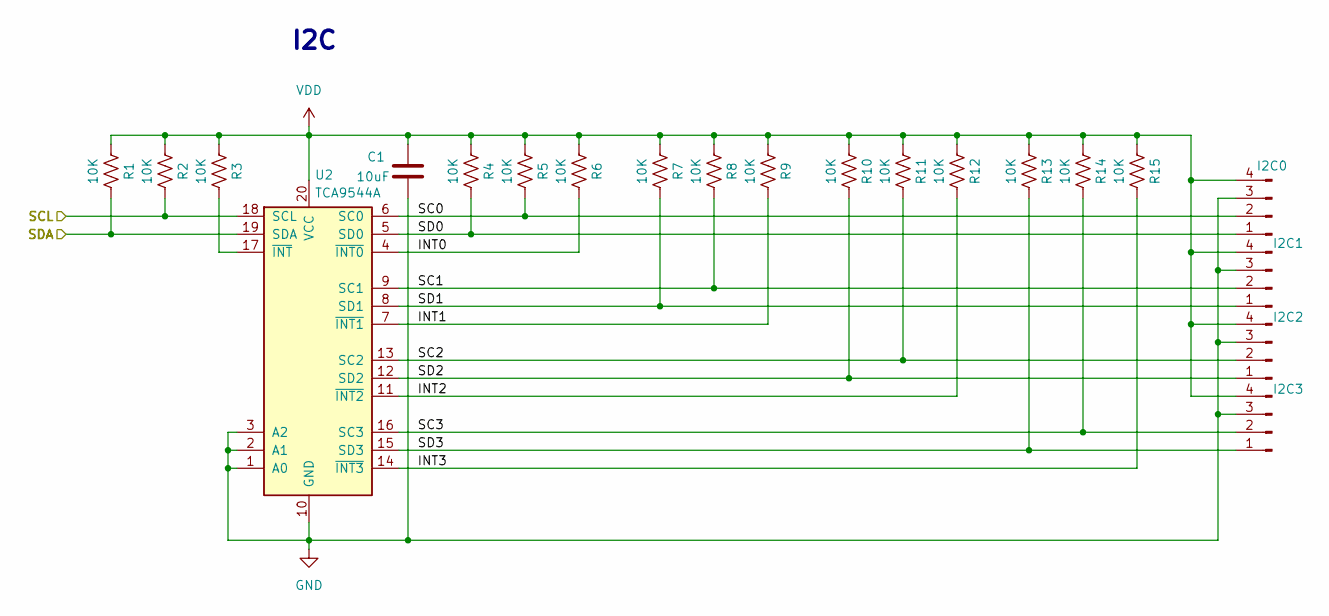
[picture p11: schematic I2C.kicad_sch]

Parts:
C1: 10uF; C_0805_2012Metric_Pad1.18x1.45mm_HandSolder
I2C0, I2C1, I2C2, I2C3: Conn_01x04_Pin; Molex_KK-254_AE-6410-04A_1x04_P2.54mm_Vertical
R1, R2, R3, R4, R5, R6, R7, R8, R9, R10, R11, R12, R13, R14, R15: 10K; R_0805_2012Metric_Pad1.20x1.40mm_HandSolder
U2: TCA9544A; TSSOP-20_4.4x6.5mm_P0.65mm

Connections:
/I2C/INT0: R6.2, U2.4 (~INT0)
/I2C/INT1: R9.2, U2.7 (~INT1)
/I2C/INT2: R12.2, U2.11 (~INT2)
/I2C/INT3: R15.2, U2.14 (~INT3)
/I2C/SC0: I2C0.2, R5.2, U2.6 (SC0)
/I2C/SC1: I2C1.2, R8.2, U2.9 (SC1)
/I2C/SC2: I2C2.2, R11.2, U2.13 (SC2)
/I2C/SC3: I2C3.2, R14.2, U2.16 (SC3)
/I2C/SD0: I2C0.1, R4.2, U2.5 (SD0)
/I2C/SD1: I2C1.1, R7.2, U2.8 (SD1)
/I2C/SD2: I2C2.1, R10.2, U2.12 (SD2)
/I2C/SD3: I2C3.1, R13.2, U2.15 (SD3)
/SCL: R2.2, U2.18 (SCL); also elsewhere on the board
/SDA: R1.2, U2.19 (SDA); also elsewhere on the board
GND: C1.2, I2C0.3, I2C1.3, I2C2.3, I2C3.3, U2.1 (A0), U2.2 (A1), U2.3 (A2), U2.10 (GND); also elsewhere on the board
unnamed: R3.2, U2.17 (~INT)
VDD: C1.1, I2C0.4, I2C1.4, I2C2.4, I2C3.4, R1.1, R2.1, R3.1, R4.1, R5.1, R6.1, R7.1, R8.1, R9.1, R10.1, R11.1, R12.1, R13.1, R14.1, R15.1, U2.20 (VCC); also elsewhere on the board

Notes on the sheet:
I2C

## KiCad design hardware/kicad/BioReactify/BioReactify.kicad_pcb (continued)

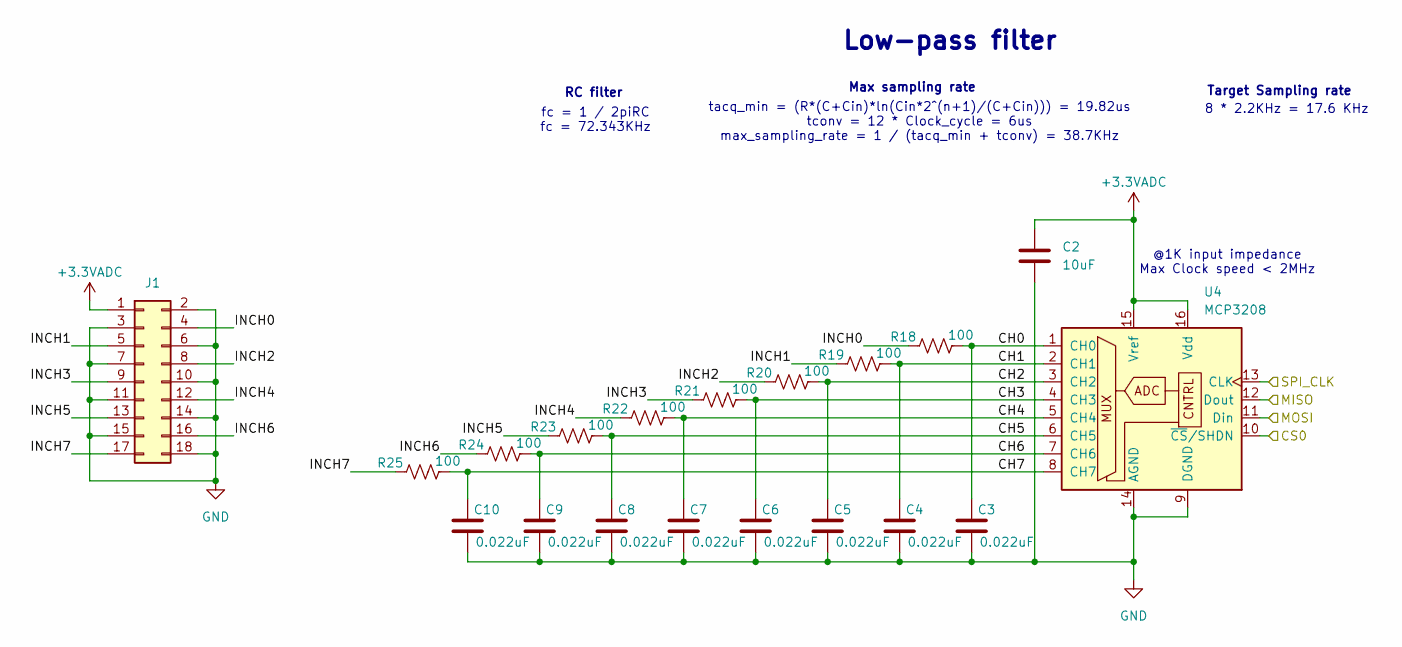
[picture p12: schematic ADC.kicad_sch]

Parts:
C2: 10uF; C_0805_2012Metric
C3, C4, C5, C6, C7, C8, C9, C10: 0.022uF; C_0805_2012Metric
J1: Conn_02x09_Odd_Even; PinHeader_2x09_P2.54mm_Vertical
R18, R19, R20, R21, R22, R23, R24, R25: 100; R_0805_2012Metric_Pad1.20x1.40mm_HandSolder
U4: MCP3208; DIP-16_W7.62mm_Socket

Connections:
+3.3VADC: C2.1, J1.1, U4.15 (Vref), U4.16 (Vdd)
/ADC/CH0: C3.1, R18.1, U4.1 (CH0)
/ADC/CH1: C4.1, R19.1, U4.2 (CH1)
/ADC/CH2: C5.1, R20.1, U4.3 (CH2)
/ADC/CH3: C6.1, R21.1, U4.4 (CH3)
/ADC/CH4: C7.1, R22.1, U4.5 (CH4)
/ADC/CH5: C8.1, R23.1, U4.6 (CH5)
/ADC/CH6: C9.1, R24.1, U4.7 (CH6)
/ADC/CH7: C10.1, R25.1, U4.8 (CH7)
/ADC/INCH0: J1.4, R18.2
/ADC/INCH1: J1.5, R19.2
/ADC/INCH2: J1.8, R20.2
/ADC/INCH3: J1.9, R21.2
/ADC/INCH4: J1.12, R22.2
/ADC/INCH5: J1.13, R23.2
/ADC/INCH6: J1.16, R24.2
/ADC/INCH7: J1.17, R25.2
/CS: U4.10 (~CS/SHDN); also elsewhere on the board
/MISO: U4.12 (Dout); also elsewhere on the board
/MOSI: U4.11 (Din); also elsewhere on the board
/SCLK: U4.13 (CLK); also elsewhere on the board
GND: C2.2, C3.2, C4.2, C5.2, C6.2, C7.2, C8.2, C9.2, C10.2, J1.2, J1.3, J1.6, J1.7, J1.10, J1.11, J1.14, J1.15, J1.18, U4.9 (DGND), U4.14 (AGND); also elsewhere on the board

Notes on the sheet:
8 * 2.2KHz = 17.6 KHz
Max sampling rate
tacq_min = (R*(C+Cin)*ln(Cin*2^(n+1)/(C+Cin))) = 19.82us tconv = 12 * Clock_cycle = 6us max_sampling_rate = 1 / (tacq_min + tconv) = 38.7KHz
fc = 1 / 2piRC fc = 72.343KHz
@1K input impedance Max Clock speed < 2MHz
Low-pass filter
RC filter
Target Sampling rate


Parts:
C11: 10uF; C_0805_2012Metric
IC1: MJ5688-B111-HR1-C; RJ45-TH_MJ5688-B111-HR1-C; Manufacturer_Part_Number MJ5688-B111-HR1-C
R16: 0; R_1206_3216Metric_Pad1.30x1.75mm_HandSolder
R17: 100; R_0805_2012Metric_Pad1.20x1.40mm_HandSolder
U3: MAX3490xSA; SOIC-8_3.9x4.9mm_P1.27mm

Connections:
/RS485/R0: R16.2, U3.2 (RO)
/RS485/RX2: R16.1; also elsewhere on the board
/RS485/RX_N: IC1.2, R17.2, U3.7 (B)
/RS485/RX_P: IC1.1, R17.1, U3.8 (A)
/RS485/TX2: U3.3 (DI); also elsewhere on the board
/RS485/TX_N: IC1.7, U3.6 (Z)
/RS485/TX_P: IC1.8, U3.5 (Y)
GND: C11.2, IC1.3, IC1.4, IC1.5, IC1.6, U3.4 (GND); also elsewhere on the board
VDD: C11.1, U3.1 (VCC); also elsewhere on the board

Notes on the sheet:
Full Duplex RS485



Board: 4 copper layers, 70.0 x 70.0 mm, 56 parts (4 on the bottom side), 56 nets.

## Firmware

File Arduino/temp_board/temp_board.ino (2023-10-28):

#include <Arduino.h>
#include "MCP_ADC.h"
#include "QuickPID.h"

boolean         newCommand = false;
String          ADDRESS = "tmp";
String          inputString = "";

unsigned long   analog[] = {0, 0, 0, 0, 0, 0, 0, 0};
float           temp[8];
float           a[8];
float           sample_number = 0;
uint32_t        sample_time = 1000000/1;
boolean         READING = false;
float           inputVoltage = 3.3;
float           refVoltage = 3.3;
int             resistorReference = 10000;

float           setpoint[] = {-100, -100, -100, -100, -100, -100, -100, -100};
float           output[8];
float           Kp = 140;
float           Ki = 0.004;
float           Kd = 1000;

#define MCP_DOUT 21
#define MCP_DIN  22
#define MCP_CLK  19
#define CS1      23

#define LEDC_CHANNEL_0 0
#define LEDC_CHANNEL_1 1
#define LEDC_CHANNEL_2 2
#define LEDC_CHANNEL_3 3
#define LEDC_CHANNEL_4 4
#define LEDC_CHANNEL_5 5
#define LEDC_CHANNEL_6 6
#define LEDC_CHANNEL_7 7

#define LEDC_BIT 8

#define LEDC_BASE_FREQ 5000

#define HEATER_PIN_0 13
#define HEATER_PIN_1 12
#define HEATER_PIN_2 14
#define HEATER_PIN_3 27
#define HEATER_PIN_4 26
#define HEATER_PIN_5 25
#define HEATER_PIN_6 33
#define HEATER_PIN_7 32

MCP3208 ADC1(MCP_DOUT, MCP_DIN, MCP_CLK);

QuickPID PID_0(&temp[0], &output[0], &setpoint[0]);
QuickPID PID_1(&temp[1], &output[1], &setpoint[1]);
QuickPID PID_2(&temp[2], &output[2], &setpoint[2]);
QuickPID PID_3(&temp[3], &output[3], &setpoint[3]);
QuickPID PID_4(&temp[4], &output[4], &setpoint[4]);
QuickPID PID_5(&temp[5], &output[5], &setpoint[5]);
QuickPID PID_6(&temp[6], &output[6], &setpoint[6]);
QuickPID PID_7(&temp[7], &output[7], &setpoint[7]);
QuickPID *allPIDS[8] = {&PID_0, &PID_1, &PID_2, &PID_3, &PID_4, &PID_5, &PID_6, &PID_7};

esp_timer_create_args_t create_args;
esp_timer_handle_t timer_handle;

void read_temp(void *p) {
  READING = true;                                                            // Change flag to enable print
}

void setup() {
  //Serial.begin(9600);
  Serial2.begin(230400, SERIAL_8N1, 16, 17);

  ADC1.begin(CS1);
  ADC1.setSPIspeed(1000000);

  ledcSetup(LEDC_CHANNEL_0, LEDC_BASE_FREQ, LEDC_BIT);
  ledcSetup(LEDC_CHANNEL_1, LEDC_BASE_FREQ, LEDC_BIT);
  ledcSetup(LEDC_CHANNEL_2, LEDC_BASE_FREQ, LEDC_BIT);
  ledcSetup(LEDC_CHANNEL_3, LEDC_BASE_FREQ, LEDC_BIT);
  ledcSetup(LEDC_CHANNEL_4, LEDC_BASE_FREQ, LEDC_BIT);
  ledcSetup(LEDC_CHANNEL_5, LEDC_BASE_FREQ, LEDC_BIT);
  ledcSetup(LEDC_CHANNEL_6, LEDC_BASE_FREQ, LEDC_BIT);
  ledcSetup(LEDC_CHANNEL_7, LEDC_BASE_FREQ, LEDC_BIT);

  ledcAttachPin(HEATER_PIN_0, LEDC_CHANNEL_0);
  ledcAttachPin(HEATER_PIN_1, LEDC_CHANNEL_1);
  ledcAttachPin(HEATER_PIN_2, LEDC_CHANNEL_2);
  ledcAttachPin(HEATER_PIN_3, LEDC_CHANNEL_3);
  ledcAttachPin(HEATER_PIN_4, LEDC_CHANNEL_4);
  ledcAttachPin(HEATER_PIN_5, LEDC_CHANNEL_5);
  ledcAttachPin(HEATER_PIN_6, LEDC_CHANNEL_6);
  ledcAttachPin(HEATER_PIN_7, LEDC_CHANNEL_7);

  ledcWrite(LEDC_CHANNEL_0, 0);
  ledcWrite(LEDC_CHANNEL_1, 0);
  ledcWrite(LEDC_CHANNEL_2, 0);
  ledcWrite(LEDC_CHANNEL_3, 0);
  ledcWrite(LEDC_CHANNEL_4, 0);
  ledcWrite(LEDC_CHANNEL_5, 0);
  ledcWrite(LEDC_CHANNEL_6, 0);
  ledcWrite(LEDC_CHANNEL_7, 0);
  delay(500);

  create_args.callback = read_temp; // Set esp-timer argument
  esp_timer_create(&create_args, &timer_handle);

  PID_0.SetMode(PID_0.Control::automatic);
  PID_1.SetMode(PID_1.Control::automatic);
  PID_2.SetMode(PID_2.Control::automatic);
  PID_3.SetMode(PID_3.Control::automatic);
  PID_4.SetMode(PID_4.Control::automatic);
  PID_5.SetMode(PID_5.Control::automatic);
  PID_6.SetMode(PID_6.Control::automatic);
  PID_7.SetMode(PID_7.Control::automatic);
  for (byte i = 0; i<8; i++){
    allPIDS[i]->SetOutputLimits(0, 255);
    allPIDS[i]->SetTunings(Kp, Ki, Kd);
  }
  esp_timer_start_once(timer_handle, sample_time);
}

void loop() {

  if (!READING){
    for (byte i = 0; i < ADC1.channels(); i++) {
      analog[i] += ADC1.analogRead(i);
    }
    sample_number += 1;
  }

  if (READING) {
    for (byte i = 0; i < ADC1.channels(); i++) {
      a[i] = analog[i] / sample_number;
      float r = resistorReference/((4095*inputVoltage/(a[i]*refVoltage))-1);
      temp[i] = (1 / ( 8.294e-4 + 2.624e-4*log(r) + 1.369e-7*pow(log(r), 3) )) - 273.15;
      analog[i] = 0;

      allPIDS[i]-> Compute();
    }
    sample_number = 0;

    ledcWrite(LEDC_CHANNEL_0, output[0]);
    ledcWrite(LEDC_CHANNEL_1, output[1]);
    ledcWrite(LEDC_CHANNEL_2, output[2]);
    ledcWrite(LEDC_CHANNEL_3, output[3]);
    ledcWrite(LEDC_CHANNEL_4, output[4]);
    ledcWrite(LEDC_CHANNEL_5, output[5]);
    ledcWrite(LEDC_CHANNEL_6, output[6]);
    ledcWrite(LEDC_CHANNEL_7, output[7]);

    //printf("%f %f %f %f %f %f %f %f\n", a[0], a[1], a[2], a[3], a[4], a[5], a[6], a[7]);
    //printf("%f %f %f %f %f %f %f %f\n", temp[0], temp[1], temp[2], temp[3], temp[4], temp[5], temp[6], temp[7]);
    //printf("%.1f %.1f %.1f %.1f %.1f %.1f %.1f %.1f\n", output[0], output[1], output[2], output[3], output[4], output[5], output[6], output[7]);
    //printf("%f %f\n", temp[1], output[1]);

    esp_timer_start_once(timer_handle, sample_time);
    READING = false;
  }
  parseSerial();
  parseString(inputString);
  inputString = "";
}

void parseSerial(void){
  while(Serial2.available()){
    char inChar = char(Serial2.read());
    inputString += inChar;
    if(inChar == '!'){
      newCommand = true;
      break;
    }
  }
}

void parseString(String inputString){
  if(newCommand){
    String ADDR = inputString.substring(0, inputString.indexOf(' '));

    if(ADDR == ADDRESS){
      int firstcomma = inputString.indexOf(',');
      String cmd = inputString.substring(inputString.indexOf(' '), firstcomma);
      int command = cmd.toInt();

      if(command == 1){
        int lastcomma = firstcomma;
        for (byte i = 0; i < 8; i++){
          int nextcomma = inputString.indexOf(',', lastcomma + 1);
          String val = inputString.substring(lastcomma + 1, nextcomma);
          float value = val.toFloat();
          setpoint[i] = value;
          lastcomma = nextcomma;
        }
        Serial2.println("115!");
      }
      else if (command == 2){
        Serial2.println("115!");
      }
      else if (command == 3){
        Serial2.println("115!");
        String sample = ADDRESS + " ";
        for(byte i = 0; i < 8; i++){
          sample = sample + "," + (String) temp[i];
        }
        sample = sample + ",115,!";
        Serial2.println(sample);
      }
    }

    inputString = "";
    newCommand = false;
  }
}

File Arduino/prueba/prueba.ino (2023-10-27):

#include <Arduino.h>
#include <stdio.h>
#include "freertos/FreeRTOS.h"
#include "freertos/portmacro.h"
#include "freertos/task.h"
#include "freertos/queue.h"
#include "driver/periph_ctrl.h"
#include "driver/ledc.h"
#include "driver/gpio.h"
#include "driver/pcnt.h"
#include "esp_attr.h"
#include "esp_log.h"
#include "QuickPID.h"

int16_t   pulses[8];
float     rpm[8];
uint32_t  sample_time = 1000000/4;
boolean   READING = true;

boolean   newCommand = false;
String    ADDRESS = "stir";
String    inputString = "";

float setpoint[] = {0,0,0,0,0,0,0,0};
float output[8];
float Kp = 0.005;
float Ki = 0.17;
float Kd = 0.001;

// use first channel of 16 channels (started from zero)
#define LEDC_CHANNEL_0 0
#define LEDC_CHANNEL_1 1
#define LEDC_CHANNEL_2 2
#define LEDC_CHANNEL_3 3
#define LEDC_CHANNEL_4 4
#define LEDC_CHANNEL_5 5
#define LEDC_CHANNEL_6 6
#define LEDC_CHANNEL_7 7

// use 8 bit precission for LEDC timer
#define LEDC_BIT 8

// use 5000 Hz as a LEDC base frequency
#define LEDC_BASE_FREQ 4000

// fade LED PIN (replace with LED_BUILTIN constant for built-in LED)
#define MOTOR_PIN_0 13
#define MOTOR_PIN_1 14
#define MOTOR_PIN_2 27
#define MOTOR_PIN_3 26
#define MOTOR_PIN_4 25
#define MOTOR_PIN_5 33
#define MOTOR_PIN_6 32
#define MOTOR_PIN_7 23

// fade LED PIN (replace with LED_BUILTIN constant for built-in LED)
#define TACHOMETER_PIN_0 35
#define TACHOMETER_PIN_1 34
#define TACHOMETER_PIN_2 39
#define TACHOMETER_PIN_3 36
#define TACHOMETER_PIN_4 15
#define TACHOMETER_PIN_5 4
#define TACHOMETER_PIN_6 18
#define TACHOMETER_PIN_7 19

xQueueHandle pcnt_evt_queue;   // A queue to handle pulse counter events
pcnt_isr_handle_t user_isr_handle = NULL; //user's ISR service handle

esp_timer_create_args_t create_args;                                  
esp_timer_handle_t timer_handle;

QuickPID PID_0(&rpm[0], &output[0], &setpoint[0]);
QuickPID PID_1(&rpm[1], &output[1], &setpoint[1]);
QuickPID PID_2(&rpm[2], &output[2], &setpoint[2]);
QuickPID PID_3(&rpm[3], &output[3], &setpoint[3]);
QuickPID PID_4(&rpm[4], &output[4], &setpoint[4]);
QuickPID PID_5(&rpm[5], &output[5], &setpoint[5]);
QuickPID PID_6(&rpm[6], &output[6], &setpoint[6]);
QuickPID PID_7(&rpm[7], &output[7], &setpoint[7]);
QuickPID *allPIDS[8] = {&PID_0, &PID_1, &PID_2, &PID_3, &PID_4, &PID_5, &PID_6, &PID_7};

/* A sample structure to pass events from the PCNT
 * interrupt handler to the main program.
 */
typedef struct {
    int unit;  // the PCNT unit that originated an interrupt
    uint32_t status; // information on the event type that caused the interrupt
    unsigned long timeStamp; // The time the event occured
} pcnt_evt_t;

/* Decode what PCNT's unit originated an interrupt
 * and pass this information together with the event type
 * and timestamp to the main program using a queue.
 */
static void IRAM_ATTR pcnt_intr_handler(void *arg)
{
    unsigned long currentMillis = millis(); //Time at instant ISR was called
    uint32_t intr_status = PCNT.int_st.val;
    int i = 0;
    pcnt_evt_t evt;
    portBASE_TYPE HPTaskAwoken = pdFALSE;

    
    for (i = 0; i < PCNT_UNIT_MAX; i++) {
        if (intr_status & (BIT(i))) {
            evt.unit = i;
            /* Save the PCNT event type that caused an interrupt
               to pass it to the main program */
            evt.status = PCNT.status_unit[i].val;
            evt.timeStamp = currentMillis; 
            PCNT.int_clr.val = BIT(i);
            xQueueSendFromISR(pcnt_evt_queue, &evt, &HPTaskAwoken);
            if (HPTaskAwoken == pdTRUE) {
                portYIELD_FROM_ISR();
            }
        }
    }
}


/* Initialize PCNT functions for one channel:
 */

void pcnt_init_channel(pcnt_unit_t PCNT_UNIT, int PCNT_INPUT_SIG_IO, pcnt_channel_t PCNT_CHANNEL = PCNT_CHANNEL_0, int PCNT_H_LIM_VAL = 20000) {
    /* Prepare configuration for the PCNT unit */
    pcnt_config_t pcnt_config; 
        // Set PCNT input signal and control GPIOs
        pcnt_config.pulse_gpio_num = PCNT_INPUT_SIG_IO;
        pcnt_config.ctrl_gpio_num = 22;
        pcnt_config.channel = PCNT_CHANNEL;
        pcnt_config.unit = PCNT_UNIT;
        // What to do on the positive / negative edge of pulse input?
        pcnt_config.pos_mode = PCNT_COUNT_INC;   // Count up on the positive edge
        pcnt_config.neg_mode = PCNT_COUNT_DIS;   // Keep the counter value on the negative edge
        // What to do when control input is low or high?
        pcnt_config.lctrl_mode = PCNT_MODE_DISABLE; // Reverse counting direction if low
        pcnt_config.hctrl_mode = PCNT_MODE_KEEP;    // Keep the primary counter mode if high
        // Set the maximum and minimum limit values to watch
        pcnt_config.counter_h_lim = PCNT_H_LIM_VAL;
        pcnt_config.counter_l_lim = -1;
    
    /* Initialize PCNT unit */
    pcnt_unit_config(&pcnt_config);
    /* Configure and enable the input filter */
    pcnt_set_filter_value(PCNT_UNIT, 100);
    pcnt_filter_enable(PCNT_UNIT);

    /* Enable events on zero, maximum and minimum limit values */
    pcnt_event_disable(PCNT_UNIT, PCNT_EVT_ZERO);
    pcnt_event_enable(PCNT_UNIT, PCNT_EVT_H_LIM);
    pcnt_event_disable(PCNT_UNIT, PCNT_EVT_L_LIM);

    /* Initialize PCNT's counter */
    pcnt_counter_pause(PCNT_UNIT);
    pcnt_counter_clear(PCNT_UNIT);
    
    /* Register ISR handler and enable interrupts for PCNT unit */
    pcnt_isr_register(pcnt_intr_handler, NULL, 0, &user_isr_handle);
    pcnt_intr_enable(PCNT_UNIT);

    /* Everything is set up, now go to counting */
    pcnt_counter_resume(PCNT_UNIT);
}

void read_PCNT(void *p) {
  READING = true;                                                            // Change flag to enable print
}

void setup() {
  Serial.begin(9600);
  
  ledcSetup(LEDC_CHANNEL_0, LEDC_BASE_FREQ, LEDC_BIT);
  ledcSetup(LEDC_CHANNEL_1, LEDC_BASE_FREQ, LEDC_BIT);
  ledcSetup(LEDC_CHANNEL_2, LEDC_BASE_FREQ, LEDC_BIT);
  ledcSetup(LEDC_CHANNEL_3, LEDC_BASE_FREQ, LEDC_BIT);
  ledcSetup(LEDC_CHANNEL_4, LEDC_BASE_FREQ, LEDC_BIT);
  ledcSetup(LEDC_CHANNEL_5, LEDC_BASE_FREQ, LEDC_BIT);
  ledcSetup(LEDC_CHANNEL_6, LEDC_BASE_FREQ, LEDC_BIT);
  ledcSetup(LEDC_CHANNEL_7, LEDC_BASE_FREQ, LEDC_BIT);
  
  ledcAttachPin(MOTOR_PIN_0, LEDC_CHANNEL_0);
  ledcAttachPin(MOTOR_PIN_1, LEDC_CHANNEL_1);
  ledcAttachPin(MOTOR_PIN_2, LEDC_CHANNEL_2);
  ledcAttachPin(MOTOR_PIN_3, LEDC_CHANNEL_3);
  ledcAttachPin(MOTOR_PIN_4, LEDC_CHANNEL_4);
  ledcAttachPin(MOTOR_PIN_5, LEDC_CHANNEL_5);
  ledcAttachPin(MOTOR_PIN_6, LEDC_CHANNEL_6);
  ledcAttachPin(MOTOR_PIN_7, LEDC_CHANNEL_7);
  
  ledcWrite(LEDC_CHANNEL_0, 0);
  ledcWrite(LEDC_CHANNEL_1, 0);
  ledcWrite(LEDC_CHANNEL_2, 0);
  ledcWrite(LEDC_CHANNEL_3, 0);
  ledcWrite(LEDC_CHANNEL_4, 0);
  ledcWrite(LEDC_CHANNEL_5, 0);
  ledcWrite(LEDC_CHANNEL_6, 0);
  ledcWrite(LEDC_CHANNEL_7, 0);
  delay(500);
  
    /* Initialize PCNT event queue and PCNT functions */
  pcnt_evt_queue = xQueueCreate(10, sizeof(pcnt_evt_t));
  pcnt_init_channel(PCNT_UNIT_0, TACHOMETER_PIN_0);
  pcnt_init_channel(PCNT_UNIT_1, TACHOMETER_PIN_1);
  pcnt_init_channel(PCNT_UNIT_2, TACHOMETER_PIN_2);
  pcnt_init_channel(PCNT_UNIT_3, TACHOMETER_PIN_3);
  pcnt_init_channel(PCNT_UNIT_4, TACHOMETER_PIN_4);
  pcnt_init_channel(PCNT_UNIT_5, TACHOMETER_PIN_5);
  pcnt_init_channel(PCNT_UNIT_6, TACHOMETER_PIN_6);
  pcnt_init_channel(PCNT_UNIT_7, TACHOMETER_PIN_7);

  create_args.callback = read_PCNT; // Set esp-timer argument
  esp_timer_create(&create_args, &timer_handle);
  
  PID_0.SetMode(PID_0.Control::automatic);
  PID_1.SetMode(PID_1.Control::automatic);
  PID_2.SetMode(PID_2.Control::automatic);
  PID_3.SetMode(PID_3.Control::automatic);
  PID_4.SetMode(PID_4.Control::automatic);
  PID_5.SetMode(PID_5.Control::automatic);
  PID_6.SetMode(PID_6.Control::automatic);
  PID_7.SetMode(PID_7.Control::automatic);
  for (byte i = 0; i<8; i++){
    allPIDS[i]->SetOutputLimits(0, 255);
    allPIDS[i]->SetTunings(Kp, Ki, Kd);
  }
}
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

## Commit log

2023-11-06 incomplete MHE
    [pumps.tsv, timers.csv, vial.tsv]
2023-11-07 complete mhe stirrer
    [data.csv, parameters.csv, stirrer_rate.csv, vial.tsv]
2023-11-09 Methods for reactor temperature PID calibration
    [pwm_value.csv]
2023-11-11 Fixed MHE for reactor electric heater
    [data.csv, parameters.csv, pwm_value.csv]
2023-11-15 Added reactor control files
    [data.csv, oxygen_bounds.csv, pwm_value.csv, temp_setpoint.csv]
2024-01-16 updated heat balance model and pid
    [data.csv, oxygen_bounds.csv, pwm_value.csv, temp_setpoint.csv]
2024-01-18 Up to 8 ON/OFF timers in parallel
    [pwm_value.csv]
2024-01-22 low pass filter on T_reactor
2024-01-24 prototype flow meter
2024-03-03 board v302 prototype, classes board, exp, sqlite
    [calibracion_ph_o2.xlsx, data.csv, oxygen_bounds.csv, parameters.csv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]
2024-03-03 case PID, missing: initialize filter, turn pid on/off, link control_var
2024-03-04 completed toggle control in arduino, missing toggle control in python
2024-03-06 slaves comms config update prototype, missing: slaves info request
2024-03-06 setup logger, missing: slaves info request prototype
2024-03-10 board.reconnect(), set save period, minor bugs
2024-03-24 slaves serial comms, update missing to python board_info and get_data
2024-03-25 class Sensors(i2c,spi),dualcore-serialcomms,missing:update python comms
    [biomas_1s.csv]
2024-03-27 flow sensor, missing: flow sensor test, save_data
2024-04-01 missing: flow sensor/save_data test, serial send_data frequency eval
    [BioReactify.kicad_pcb, BioReactify.kicad_sch, analogs.kicad_sch, i2c.kicad_sch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]
2024-04-02 fully tested: flowsensor, slavescoms(slaverequest:200ms), savedata :)
    [BioReactify.kicad_pcb, BioReactify.kicad_sch, analogs.kicad_sch, i2c.kicad_sch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]
2024-04-08 espnow prototype
    [BioReactify.kicad_pcb, smart_sleeve.kicad_pcb, smart_sleeve.kicad_sch]
2024-05-16 Output class in cpp; Connect 2 boards to 1 experiment
    [BioReactify.kicad_pcb, BioReactify.kicad_sch, i2c.kicad_sch]
2024-05-20 Added diff_press sensor (sen0343)
2024-05-26 update pcb: incomplete
    [BioReactify.kicad_pcb, BioReactify.kicad_sch, adc0.kicad_sch, i2c.kicad_sch]
2024-06-13 PCB complete, biomass sensor PCB complete
    [BioReactify.kicad_pcb, BioReactify.kicad_sch, adc0.kicad_sch, analogs.kicad_sch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]
2024-06-26 Hardware updated
    [ADC.kicad_sch, BioReactify-B_Cu.gbr, BioReactify-B_Mask.gbr, BioReactify-B_Paste.gbr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]
2024-07-04 created inputs class, added DAC channels
    [ADC.kicad_sch, BioReactify-B_Cu.gbr, BioReactify-B_Mask.gbr, BioReactify-B_Paste.gbr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]
2024-07-08 new sensors; bug fix;
2024-07-16 ESP32 examples
2024-08-04 bug fix; reactor board update;
    [analog_input.kicad_sch, heating_element.kicad_pcb, reactor.kicad_pcb, reactor.kicad_sch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]
